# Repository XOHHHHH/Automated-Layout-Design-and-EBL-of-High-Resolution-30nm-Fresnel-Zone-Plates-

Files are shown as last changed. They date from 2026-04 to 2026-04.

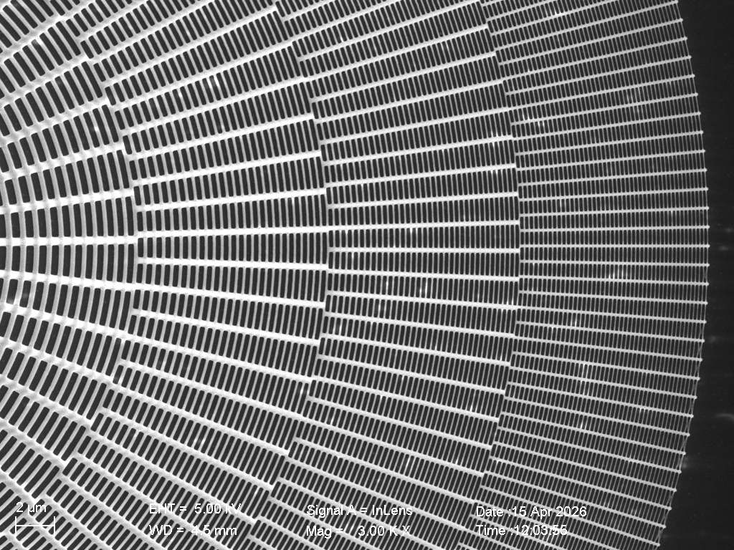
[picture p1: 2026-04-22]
05_Characterization/100nmZP-3-03.tif

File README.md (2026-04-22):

# Automated-Layout-Design-and-EBL-of-High-Resolution-30nm-Fresnel-Zone-Plates-
从自动化CAD脚本（626根参数化支撑筋）到超净间电子束光刻（EBL）实操：30nm高分辨率菲涅尔波带片全流程工程实录。内含蒙特卡洛仿真与3D邻近效应修正。From automated CAD scripting (626 spokes) to cleanroom EBL fabrication: a complete engineering workflow for 30nm high-resolution Fresnel Zone Plates, featuring Monte Carlo simulation and 3D PEC.
# Fabrication of 30nm Fresnel Zone Plate

本项目记录了在复旦大学陈宜方教授实验室完成的高分辨率菲涅尔波带片（FZP）全流程制备。通过 626 根参数化支撑筋，成功解决了 500nm 厚 HSQ 胶在 16.6:1 高深宽比下的倒塌难题，并完成了 SEM 表征。

## 1. Specifications
- **Device:** Fresnel Zone Plate (Radius: 50 μm)
- **Resolution:** ~30 nm (Outer-most zone)
- **Substrate:** 100 nm Si3N4 membrane
- **Resist:** 500 nm HSQ
- **Equipment:** JEOL JBX-6300FS (100 kV)

## 2. Workflow

### 2.1 Layout Design (AutoCAD)
为防止高深宽比的 HSQ 胶在显影时倒塌，采用参数化脚本（`.scr`）生成了 626 根渐变加强筋：
- 10-20 μm: 50 spokes, 0.5 μm width
- 20-30 μm: 94 spokes, 0.4 μm width
- 30-40 μm: 168 spokes, 0.3 μm width
- 40-50 μm: 314 spokes, 0.2 μm width
最终整合并导出为 `.dxf` 格式。

### 2.2 Simulation (GenISys TRACER)
基于 100 kV 电子束在 500nm HSQ / 100nm Si3N4 体系下的蒙特卡洛仿真，提取点扩散函数，生成 `.lpsf` 文件。

### 2.3 Proximity Effect Correction (GenISys BEAMER)
处理 `.dxf` 版图：
1. **Heal:** 融合圆环与加强筋的重叠区域，防止重复曝光。
2. **3D PEC:** 导入 `.lpsf` 数据，对外圈高密度区域进行剂量修正。
3. **Export:** 导出为 JEOL 识别的 `.v30` 格式 (EOS6 Mode, 500 pA)。

### 2.4 Job Deck Configuration (JDF/SDF)
配置 `.jdf` 脚本，设置 500 至 3200 μC/cm² 的剂量阵列（Dose array），用于测试 HSQ 的最佳曝光剂量。

### 2.5 Fabrication Process (Cleanroom)
- **Exposure:** 100kV, EOS6 (500 pA)
- **Development (HSQ 热显影):** - Developer: TMAH : H2O = 1 : 3
  - Temperature: 65 °C
  - Time: 3 min
- **Fixing (定影):**
  - Fixer: DI Water
  - Time: 30 s

## 3. Results (SEM Characterization)
通过 SEM 扫描电镜观察，30nm 最外圈线条清晰、完整，未见明显倒塌或粘连。支撑筋与波带片圆环交接处 Heal 处理良好。

## 4. Directory Structure
- `01_CAD_Design/`: `.scr` 生成脚本及 `.dxf` 最终版图
- `02_Simulation_Tracer/`: 仿真参数及 `.lpsf` 文件
- `03_PEC_Beamer/`: PEC 工程文件及导出的 `.v30` 数据
- `04_Exposure_Scripts/`: JEOL 曝光机控制脚本 `.jdf` / `.sdf`
- `05_Characterization/`: SEM 原始图片及分析结果

---
*Special thanks to Senior Student Xunjia Zhao and Prof. Yifang Chen for their expert guidance.*

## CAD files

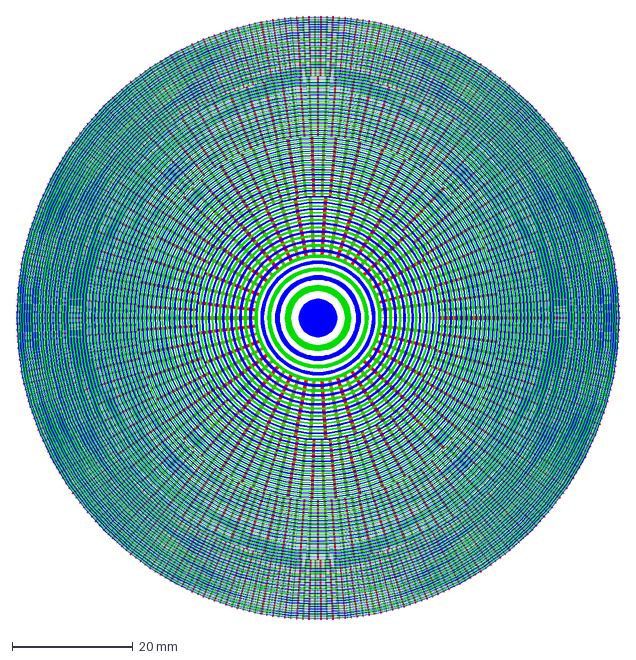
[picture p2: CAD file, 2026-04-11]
01_CAD_Design/Drawing3.dxf
100.0 x 100.0 mm

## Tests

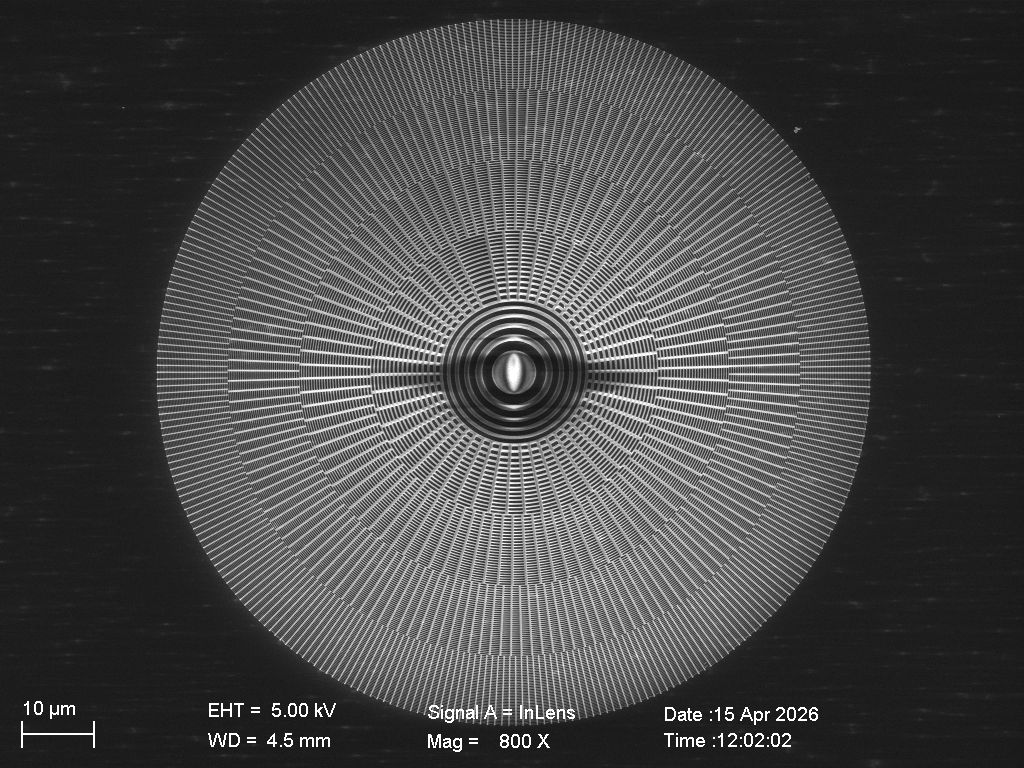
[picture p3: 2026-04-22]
05_Characterization/100nmZP-3-00.tif
